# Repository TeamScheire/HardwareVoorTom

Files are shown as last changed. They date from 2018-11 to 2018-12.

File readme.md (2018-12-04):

# Hardware hack voor microfoon

Hardware hack om een draadloze microfoon te bedienen met een grote knop in een heuptas.

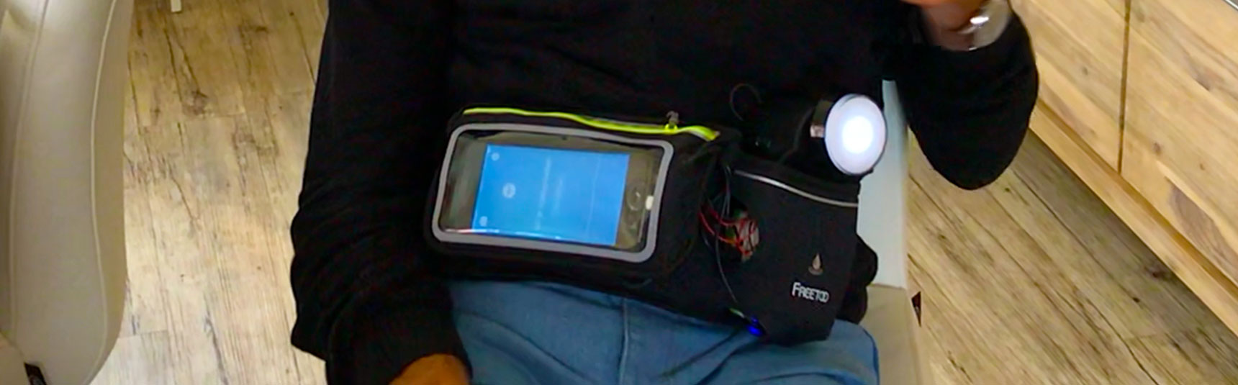
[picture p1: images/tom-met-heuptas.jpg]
heuptas


De hele set-up gaat er voor zorgen dat je op een smartphone een externe micro én een luidspreker kan aansluiten via de koptelefoon ingang. _Voor de nieuwere iphones heb je het [adaptor tussenstuk](https://www.apple.com/be-nl/shop/product/MMX62ZM/A/lightning-naar-35%E2%80%91mm-koptelefoonaansluiting-adapter) nodig._

## Beetje achtergrondinformatie over jacks

De hoofdtelefoon ingang van een smartphone is van het [type 3,5mm 'jack'](https://nl.wikipedia.org/wiki/Klink_(stopcontact)), ook wel mini-jack genoemd. Een stereo hoofdtelefoon heeft drie ringen of polen, een headset voor een smartphone waar ook een micro bij zit, heeft vier ringen.

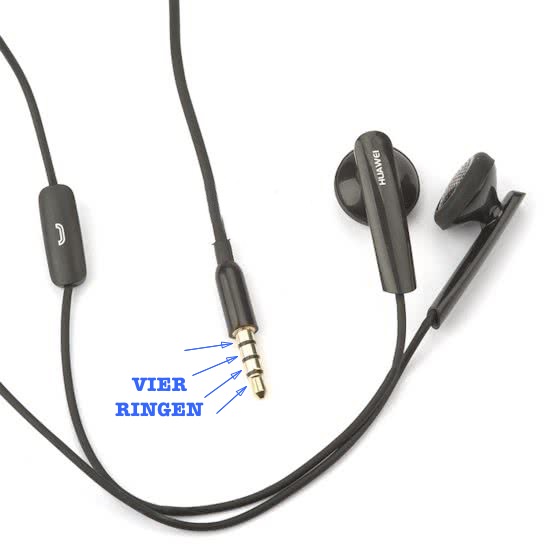
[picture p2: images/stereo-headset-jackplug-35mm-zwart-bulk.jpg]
headset


Via deze ene stekker gaat dus zowel het geluid van de microfoon naar de smartphone als van de smartphone naar de oortjes.

Om nu een aparte micro en een aparte luidspreker aan te sluiten, hebben we een splitter nodig. Via deze kabel wordt de micro en luidspreker van elkaar gescheiden.

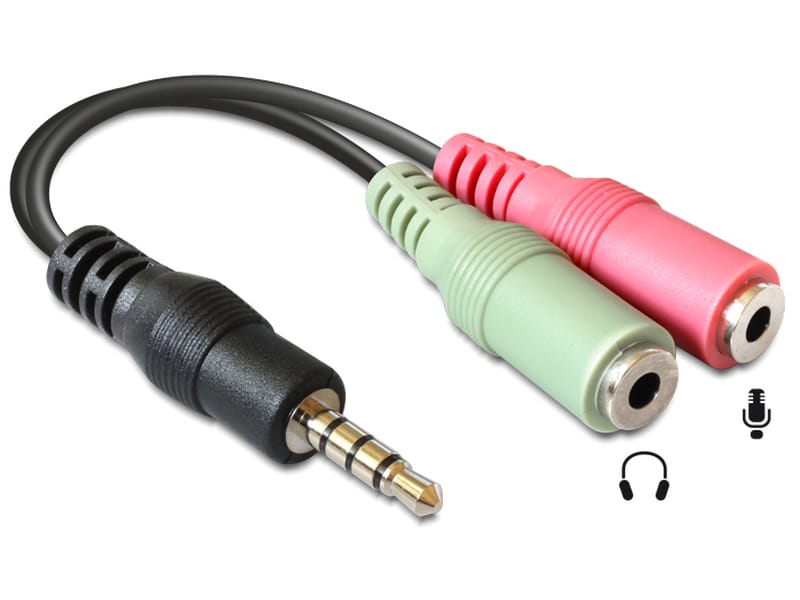
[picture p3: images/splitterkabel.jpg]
splitter


## Onderdelen in de oplossing van Tom

### Materialen voor micro en luidspreker op smartphone aan te sluiten
- Heuptas. [deze](https://www.amazon.com/gp/product/B074BRTNDD/ref=oh_aui_detailpage_o06_s01) had genoeg plaats en compartimenten voor alle onderdelen.
- Luidspreker op batterijen: [deze werd gebruikt](https://www.amazon.de/gp/product/B0721W7CTT/ref=oh_aui_detailpage_o02_s00) De micro die hierbij zit, zou ook kunnen gebruikt worden, maar voor Tom was de draad een extra hinderpaal.
- Audio splitter cable. Overal te krijgen, ook in China via deze [link](https://nl.aliexpress.com/item/New-3-5mm-Stereo-Headphone-Microphone-Audio-Y-Splitter-Cable-Adapter-Plug-Jack-Cord/32391434939.html)
- Korte stereo audio kabel. Neem er best een waarbij één van de twee stekkers in een hoek staat. Zo één als [deze](images/audio-kabel.jpg) bijvoorbeeld.
- Draadloze microfoon: Deze [relatief goedkope](https://de.aliexpress.com/item/2-4G-Wireless-Mikrofon-Lautsprecher-40-mt-bertragung-Dual-Ohr-Headset-Megaphon-Radio-Mic-F-r/32877216169.html) werd gebruikt voor Tom.

### Knop voor Tom + aansturing
- [button met ingebouwde led](https://www.adafruit.com/product/1192)
- [adafruit gemma](https://www.adafruit.com/product/1222)
- stukje prototype pcb
- draadjes
- npn-transistor
- 1k weerstand
- Kleine schuifschakelaar
- battery pack (met 3.3v lipo battery)
- 3D printed button houder: [ontwerp staat hier](designs/button-holder.stl)

## Aansluitingen

Een eenvoudige manier om de mcirofoon aan en uit te zetten is om de schakelaar in de ontvanger te gaan aansturen via een transistor die op zijn beurt via een arduino aangestuurd wordt.

Mocht er een grote knop bestaan die ingedrukt bleef, dan hadden we de arduino niet nodig, maar deze hebben we sîjtig genoeg niet gevonden.

### draadloze ontvanger
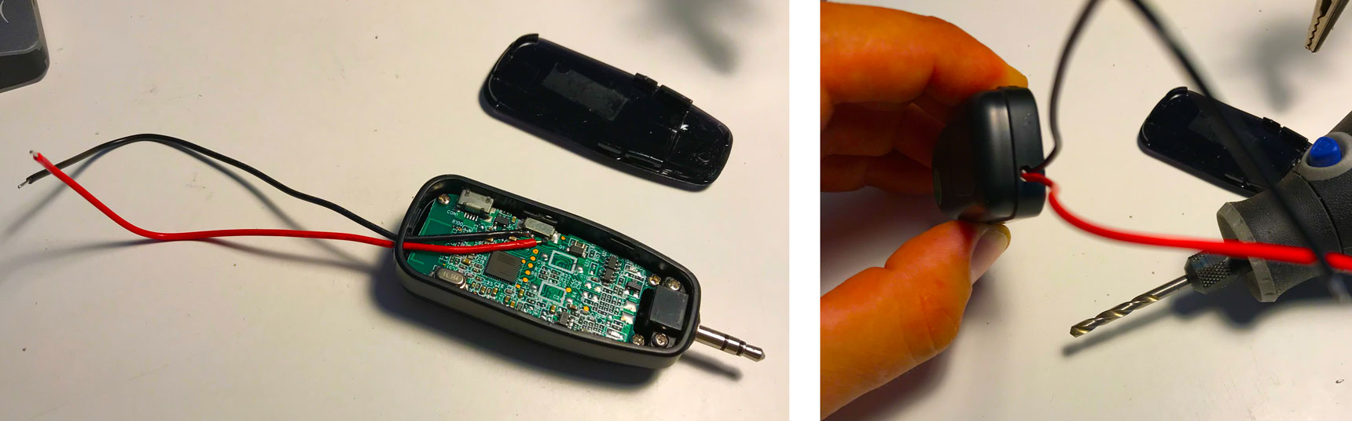
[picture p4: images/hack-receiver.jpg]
receiver


De ontvanger gaat gemakkelijk open. Je kan de pcb er ook eenvoudig uithalen om er voorzichtig twee draadjes op te solderen op de plaatsen waar de schakelaar op de printplaat vast zit.

Met een dremel boor je een gat in de behuizing. Daarna kan je alles voorzichtig terug in elkaar steken.

Je kan het testen door de twee draadjes met elkaar te verbinden. Hierdoor zet je de ontvanger aan (er gaat een klein blauw ledje knipperen).

### Knop
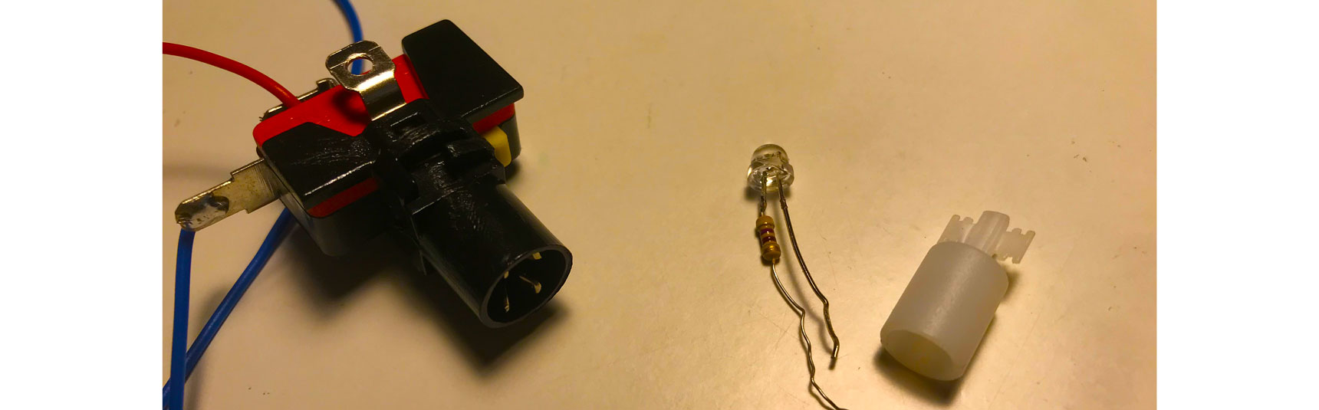
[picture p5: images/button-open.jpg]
open button


De led in de knop heeft een weerstand en is voorzien voor 5v. We gaan werken op 3.3v dus moeten we deze vervangen (of weglaten).

Je kan de knop voorzichtig open doen. De windingen van de voetjes van de led wegdraaien en de weerstand los solderen. Onthou best even de richting zodat je de led met de juiste polariteit kan terugsteken.

### batterij
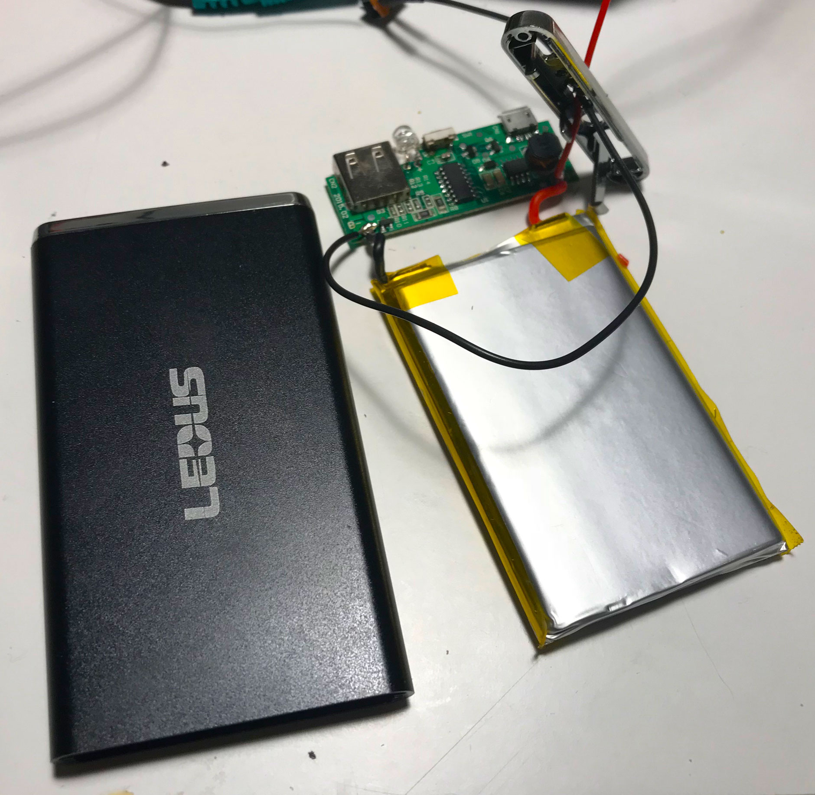
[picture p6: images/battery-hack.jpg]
batterij


Om de gemma en de knop te voeden hebben we stroom nodig. Een eerste poging om af te tappen van de luidspreker leverde heel veel gebrom op in het geluid aangezien de stroomkringen niet gescheiden waren. Pogingen met optcouplers leverden niet veel verbetering op, dus werd gekozen voor een goedkope externe batterij in een batterypack.  

Maar aangezien de meeste batterypacks automatisch uitgaan als ze niet genoeg stroom trekken, moesten we deze hacken. In de meeste battery packs van 5v, zit een lipo batterij van 3.3v, ideaal dus om die rechtstreeks aan te sluiten.

Op deze manier kan het laadcircuit nog steeds gebruikt worden en hebben we constant 3.3v.

### Gemma
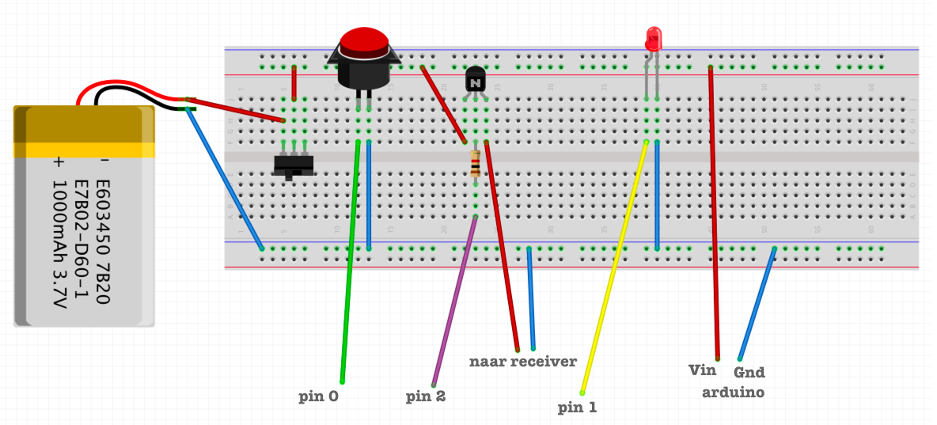
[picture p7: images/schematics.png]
schematics


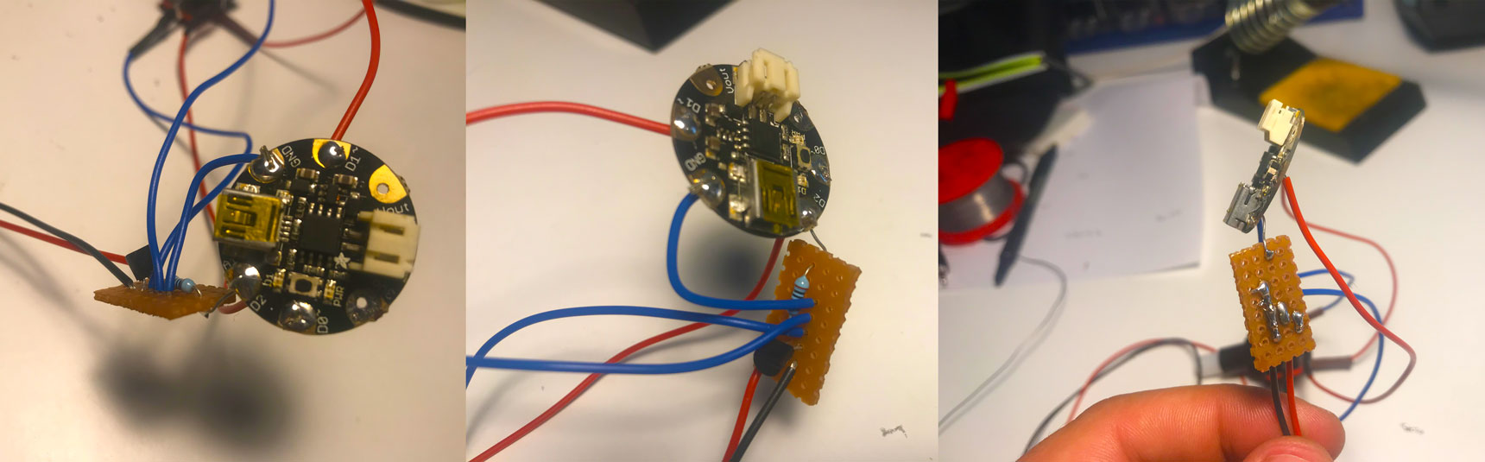
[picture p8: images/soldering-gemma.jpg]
gemma


Uploade de [code voor de arduino](button/button.ino) en soldeer de schakelingen en sluit de knop en batterij aan.

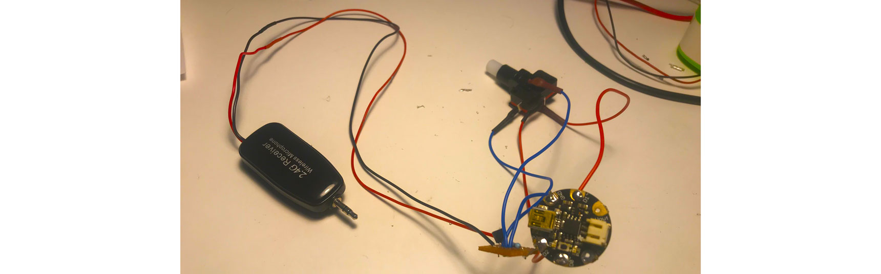
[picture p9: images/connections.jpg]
connections


### Houder

In de houder ([stl-file](designs/button-holder.stl)) kan je de knop en schuifschakelaar kwijt.

## Assemblage in de tas

- De ontvanger van de draadloze micro gaat in de rode aansluiting van de splitterkabel.
- De stereo audio kabel gaat tussen de groene aansluiting van de splitter en de luidspreker.
- De splitter gaat in de headphone aansluiting van de smartphone

Je kan alles testen met een voice-recording app op je smartphone.

Het is een beetje zoeken om alles proper in de tas te krijgen, maar op deze manier heb je een draagbare oplossing om een micro en luidspreker aan te sluiten op een smartphone en met een knop deze te activeren.

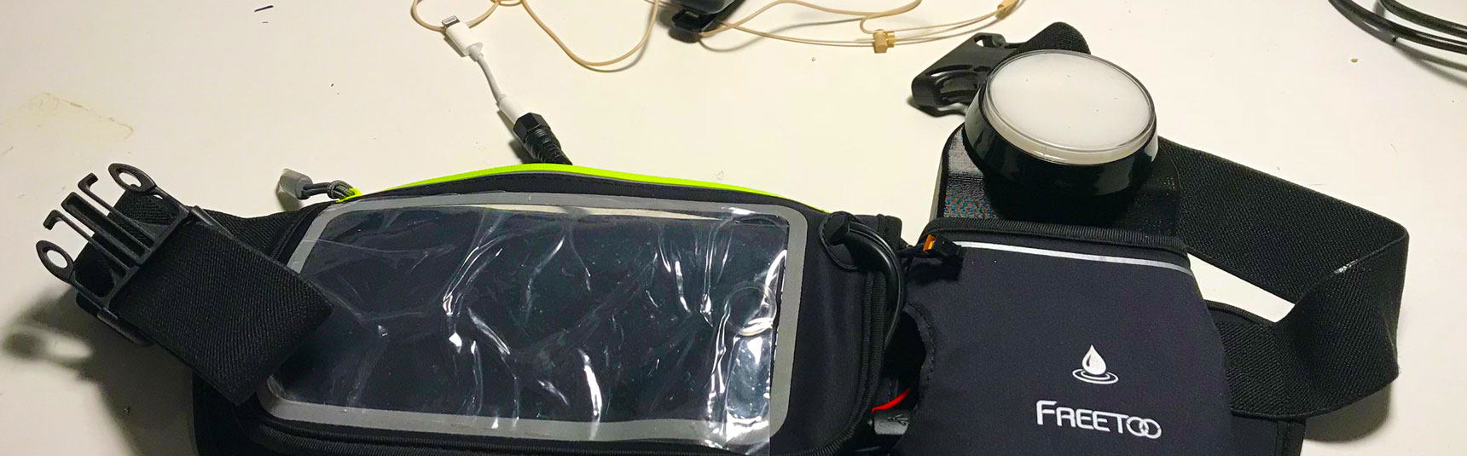
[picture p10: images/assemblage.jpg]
assemblage

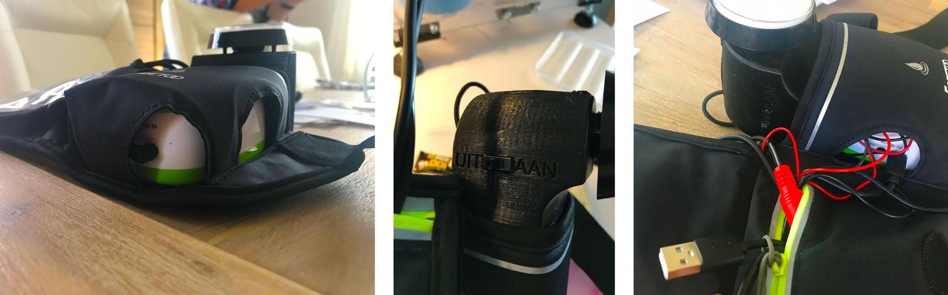
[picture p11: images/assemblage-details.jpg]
assemblage-detail


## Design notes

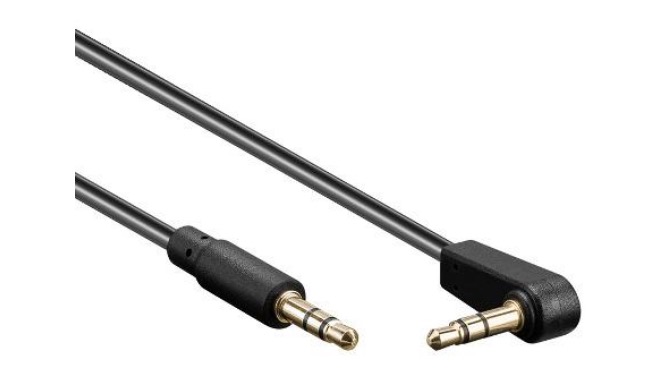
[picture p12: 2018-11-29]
images/audio-kabel.jpg

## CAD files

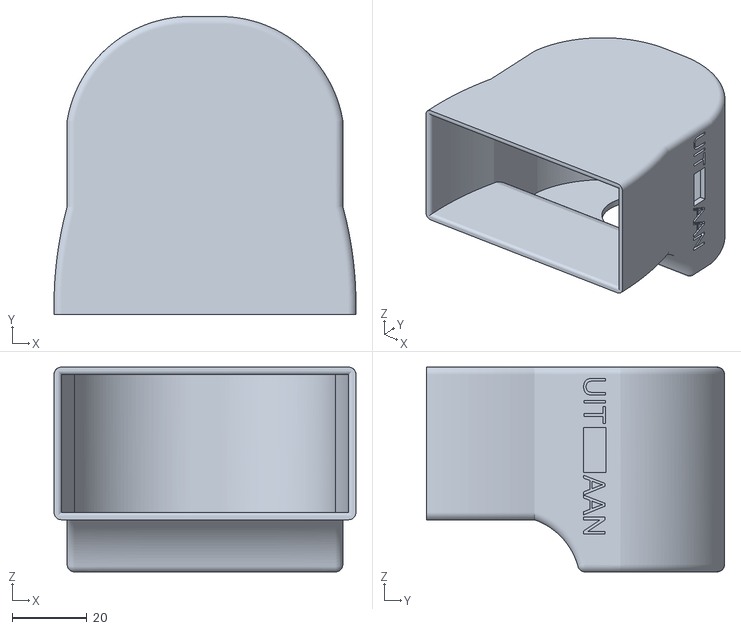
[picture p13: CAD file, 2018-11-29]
designs/button-holder.stl
81.1 x 80.0 x 55.0

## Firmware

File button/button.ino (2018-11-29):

#define BUTTON0_PIN 0
#define LED_PORT 1
int buttonPressed = 0;
int buttonStatus = 0;

#define SPEAKER_PIN 2

void setup() {
  pinMode(BUTTON0_PIN, INPUT_PULLUP);
  
  pinMode(SPEAKER_PIN, OUTPUT);
  pinMode(LED_PORT, OUTPUT);
}

void loop() {
  if (checkButtonPressed()) {
    buttonStatus = 1 - buttonStatus;
  }

  if (buttonStatus) {
    digitalWrite(SPEAKER_PIN, HIGH);
    digitalWrite(LED_PORT, HIGH);
  } else {
    digitalWrite(SPEAKER_PIN, LOW);
    digitalWrite(LED_PORT, LOW);
  }

  delay(10);
}

bool checkButtonPressed() {
  int currentValue = digitalRead(BUTTON0_PIN);
  
  if ((currentValue == LOW) && (buttonPressed == 0)) {
    buttonPressed = 1;
    return true;
  }
  if (currentValue == HIGH) {
    buttonPressed = 0;
  }
  return false;
}
